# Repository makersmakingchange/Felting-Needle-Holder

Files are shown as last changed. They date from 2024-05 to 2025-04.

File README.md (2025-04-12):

<!---  Open Source Assistive Technology: GitHub Readme Template Version 1.1 (2024-Mar-15)  --->

<!---  TITLE  --->
# Felting Needle Holder

<!---  SUMMARY  --->
The Felting Needle Holder is an open assistive technology device intended to make it easier to hold and manipulate a felting needle. The holder is ball-shaped with a diameter of 50 mm, and is comprised of four 3D printed parts. This aid is designed to be used with a felting needle that has a metal shaft with a bent end (e.g., [DIMENSIONS Replacement Felting Needles 72-73664](https://www.amazon.ca/Dimensions-Needlecrafts-Feltworks-Replacement-Felting/dp/B004W8TGIS)).

The holder consists of several 3D printed parts. No additional hardware is required. The overall cost of materials is about $1.

The Felting Needle Holder is an open assistive technology (OpenAT). Under the terms of the open source licenses, the device may be built, used, and improved upon by anyone.

Last Updated: 2024-May-16
The latest version (1.0) now includes a cover for the needle and labels to help indicate the direction to spin the ball to open or close it. The previous version (0.2) was built and tested by at least one user.

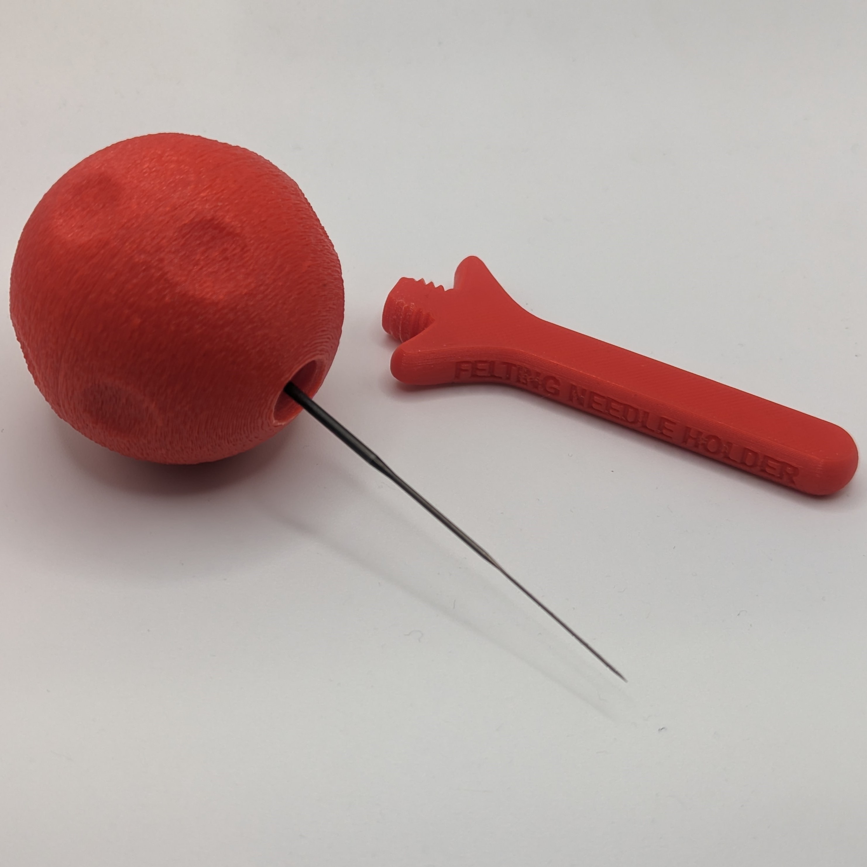
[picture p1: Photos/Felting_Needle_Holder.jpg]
A ball-shaped Felting Needle Holder.


## More info at
- [Makers Making Change Assistive Device Library Listing](https://www.makersmakingchange.com/s/product/felting-needle-holder/01tJR000004E3gVYAS)

## How to Obtain the Device
### 1. Do-it-Yourself (DIY) or Do-it-Together (DIT)

This is an open-source assistive technology, so anyone is free to build it. All of the files and instructions required to build the device are contained within this repository. Refer to the Maker Guide below.

### 2. Request a build of this device

You may also submit a build request through the [Makers Making Change Assistive Device Library Listing](https://www.makersmakingchange.com/s/product/felting-needle-holder/01tJR000004E3gVYAS) to have a volunteer maker build the device. As the requestor, you are responsible for reimbursing the maker for the cost of materials and any shipping.

### 3. Build this device for someone else

If you have the skills and equipment to build this device, and would like to donate your time to create the device for someone who needs it, visit the [MMC Maker Wanted](https://makersmakingchange.com/maker-wanted/) section.

## Build Instructions

### 1. Read through the Maker Guide

The [Maker Guide](/Documentation/Felting_Needle_Holder_Maker_Guide.pdf)  contains all the necessary information to build this device, including tool lists, assembly instructions, and testing.

### 2. Order the Off-The-Shelf Components

The [Bill of Materials](/Documentation/Felting_Needle_Holder_BOM.xlsx) lists all of the parts and components required to build the device.

### 3. Print the 3D Printable components

All of the files and individual print files can be in the [/Build_Files/3D_Printing_Files](/Build_Files/3D_Printing_Files/) folder.

### 4. Assemble the Felting Needle Holder

Reference the Assembly Guide section of the [Maker Guide](/Documentation/Felting_Needle_Holder_Maker_Guide.pdf) for the tools and steps required to build each portion.

## How to improve this Device
As open source assistive technology, you are welcomed and encouraged to improve upon the design. 

## Files
### Documentation
| Document             | Version | Link |
|----------------------|---------|------|
| Design Rationale     | 1.0     | [Felting_Needle_Holder_Design_Rationale](/Documentation/Felting_Needle_Holder_Design_Rationale.pdf)     |
| Maker Guide          | 1.0     | [Felting_Needle_Holder_Maker_Checklist](/Documentation/Felting_Needle_Holder_Maker_Guide.pdf)     |
| Bill of Materials    | 1.0     | [Felting_Needle_Holder_Bill_of_Materials](/Documentation/Felting_Needle_Holder_BOM.xlsx)     |
| User Guide           | 1.0     | [Felting_Needle_Holder_User_Guide](/Documentation/Felting_Needle_Holder_User_Guide.pdf)    |
| Changelog            | 1.0     | [Changelog](CHANGES.txt)     |

### Design Files
<!--- DESIGN FILES --->
 - [CAD Files](/Design_Files/CAD_Design_Files)

<!--- BUILD FILES --->
### Build Files
 - [3D Printing Files](/Build_Files/3D_Printing_Files)

<!--- ATTRIBUTION --->
## Attribution

This device was designed by the Neil Squire Society / Makers Making Change.

<!--- This is the attribution for the template. --->
The documentation template was created by Makers Making Change / Neil Squire Society and is used under a CC BY-SA 4.0 license. It is available at the following link: [https://github.com/makersmakingchange/OpenAT-Template](https://github.com/makersmakingchange/OpenAT-Template)

<!--- CONTRIBUTORS --->
### Contributors

 - Zee Kesler. Initial idea and design challenge.
 - Jake McIvor, Neil Squire Society. Design and documentation.

<!--- LICENSE Add the year(s) for the copyright and the Designer Name. You may use the standard set of open licenses or choose your own for the hardware, software, and accompanying materials. --->
## License
Copyright (c) 2022-2024 Neil Squire Society.

This repository describes Open Hardware:
 - Everything needed or used to design, make, test, or prepare the Felting Needle Holder is licensed under the [CERN 2.0 Weakly Reciprocal license (CERN-OHL-W v2) or later](https://cern.ch/cern-ohl ) .
 - Accompanying material such as instruction manuals, videos, and other copyrightable works that are useful but not necessary to design, make, test, or prepare the Felting Needle Holder are published under a [Creative Commons Attribution-ShareAlike 4.0 license (CC BY-SA 4.0)](https://creativecommons.org/licenses/by-sa/4.0/) .

You may redistribute and modify this documentation and make products using it under the terms of the [CERN-OHL-W v2](https://cern.ch/cern-ohl).
This documentation is distributed WITHOUT ANY EXPRESS OR IMPLIED WARRANTY, INCLUDING OF MERCHANTABILITY, SATISFACTORY QUALITY AND FITNESS FOR A PARTICULAR PURPOSE.
Please see the CERN-OHL-W v2 for applicable conditions.

Source Location: https://github.com/makersmakingchange/Felting-Needle-Holder

---

<!-- ABOUT MMC START -->
## About Makers Making Change
[Makers Making Change Logo](https://www.makersmakingchange.com/)

Makers Making Change is a program of [Neil Squire](https://www.neilsquire.ca/), a Canadian non-profit that uses technology, knowledge, and passion to empower people with disabilities.

Makers Making Change leverages the capacity of community based Makers, Disability Professionals and Volunteers to develop and deliver affordable Open Source Assistive Technologies.

 - Website: [www.MakersMakingChange.com](https://www.makersmakingchange.com/)
 - GitHub: [makersmakingchange](https://github.com/makersmakingchange)
 - Bluesky: [@makersmakingchange.bsky.social](https://bsky.app/profile/makersmakingchange.bsky.social)
 - Instagram: [@makersmakingchange](https://www.instagram.com/makersmakingchange)
 - Facebook: [makersmakechange](https://www.facebook.com/makersmakechange)
 - LinkedIn: [Neil Squire Society](https://www.linkedin.com/company/neil-squire-society/)
 - Thingiverse: [makersmakingchange](https://www.thingiverse.com/makersmakingchange/about)
 - Printables: [MakersMakingChange](https://www.printables.com/@MakersMakingChange)

### Contact Us
For technical questions, to get involved, or to share your experience we encourage you to [visit our website](https://www.makersmakingchange.com/) or [contact us](https://www.makersmakingchange.com/s/contact).
<!-- ABOUT MMC END -->

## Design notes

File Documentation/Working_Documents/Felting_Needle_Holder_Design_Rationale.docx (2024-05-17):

# Introduction

Needle felting requires a user to repeatedly insert and remove a metal felting needle into and out of the material. A holder is often used to hold one or more of the needles. Typical holders are quite narrow.

# Research

No commercially available ball shaped felting needle holders were found. A large variety of cylindrical wooden holders are available, and these are relatively cost effective (e.g., 10 for ~$20 (https://www.amazon.ca/EXCEART-Needle-Handles-Felting-Needlework/dp/B09HV1QX2X))

# Requirements

## Goals

G01 | A ball-shaped holder that is easier to grip.
G02 | No tools are required to insert, swap, and remove needle.
G03 | Minimal or no hardware.

## Functional Requirements

F01 | Device must securely hold one standard metal felting needle.
F02 | Device must allow for the needle to be swapped out for a replacement.

## Non-functional Requirement

NF01 | Design should allow for multiple sizes of holder.

## Constraints

C01 | Design released under open-source license.
C02 | Components must be manufacturable on consumer-grade FFF 3D printers.
C03 | Components must be manufacturable using commonly available FFF filaments such as PLA.

# Detailed Design

## Felting Needle

The dimensions of a DIMENSIONS felting needle (https://www.amazon.com/Dimensions-Needlecrafts-Feltworks-Replacement-Felting/dp/B004W8TGIS) were measured with a pair of digital calipers. The needle has a diameter of 1.8 mm. The top portion is bent at a 90° angle and extends about 3.5 mm from the main portion. The overall length of the needle is 78 mm.

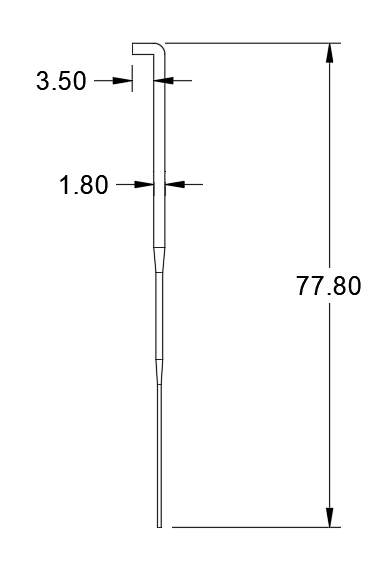
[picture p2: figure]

Figure 1: DIMENSION Felting Needle Dimensions.

## Architecture

The overall arrangement consists of four parts: Top, Bottom, Connector, and Cover. A Top and Bottom of a ball provide a larger gripping surface for the user. A Connector performs two functions: it connects the two parts of the ball together and is used to retain the needle. A Cover was later added so the ball could be stored with the needle inside with a reduce risk of either breaking the needle or the needle causing injury.

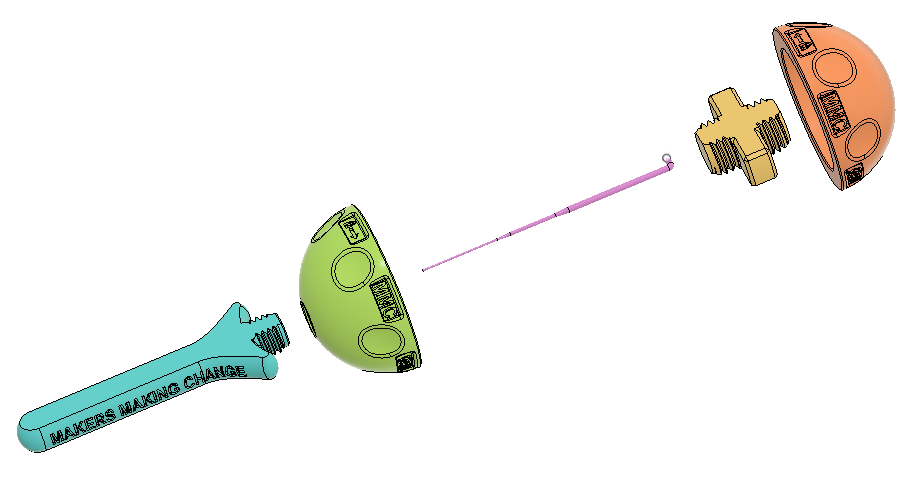
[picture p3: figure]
An exploded view of the Felting Needle Holder showing the Cover, Bottom, Needle, Connector, and Top.

Figure 2. Exploded View.

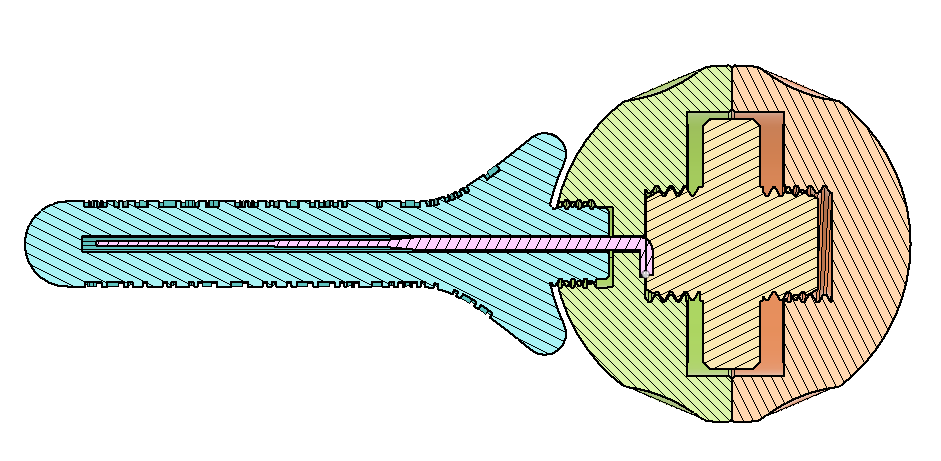
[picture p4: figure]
A cross section of the needle holder showing the needle captured by the connector

Figure 3. Felting Needle Holder Cross Section.

## Ball

The initial diameter of 50 mm for the ball was chosen based on recommendations for ergonomic handles. Additional user feedback would be helpful to determine a range of appropriate sizes for different users.

A pattern of divots was added around the ball to provide finger grips both during felting and opening and closing the ball.

Several labels were added to the ball. An arrow and a lock icon were added to provide visual indication of which direction the ball halves need to be rotated to lock it into place. An additional label was added to indicate the diameter of the ball (e.g., Ø50).

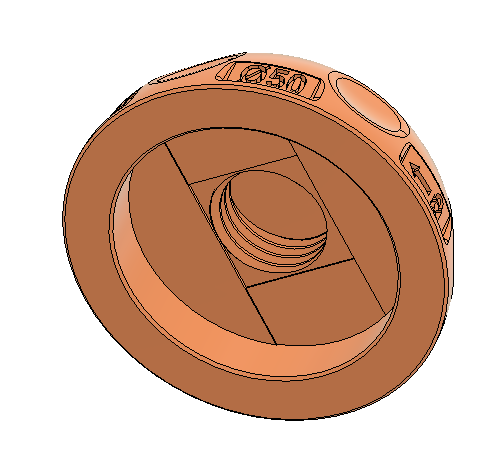
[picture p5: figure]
A CAD screenshot of the top.

Figure 4. Top Portion of Ball.

Both the top and the bottom use a right-handed M16X2 ISO Metric thread profile for the internal threads. The internal thread surfaces are offset by 0.1 mm to provide additional clearance for 3D printing.

To print without support, the inner surface of the ball has two sets of cuts to force bridging. The longest section of this bridge is 33 mm so some printers may struggle. Since these surfaces are internal, any reduced print quality is probably acceptable; those with printers that struggle to reliably bridge this distance can also enabled support.

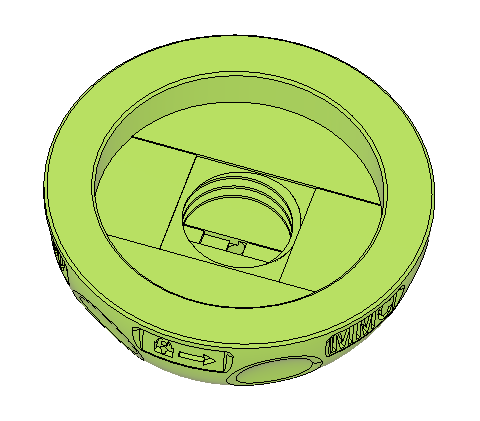
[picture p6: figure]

Figure 5. Bottom Portion of Ball.

The Bottom also has the internal thread for the connector and the corresponding bridging cuts. This side also has features for retaining and supporting the needle and connecting the cover.

The needle is retained using a cutout to fit the bent portion of the needle. This prevents the needle from rotating, and provides a surface that the Connector can compress the Needle into the Bottom. Bridging cuts were also added here to improve print quality.

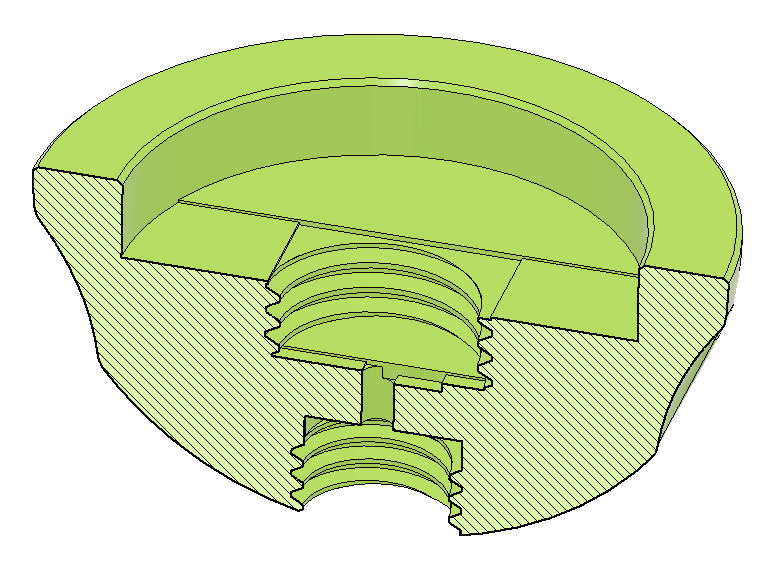
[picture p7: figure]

The bottom of the Bottom has a right-handed M12x1.75 ISO Metric internal thread to connect the Cover. These internal thread surfaces are also offset by 0.1 mm to provide additional clearance for 3D printing. The threads were made different sizes to match the smaller required size of the Cover as well as to ensure the parts can not be assembled incorrectly.

## Connector

The Connector retains the needle into the Bottom and connects the Top and Bottom. The Connector consists of two threaded portions for connecting to the top and bottom, and a middle section that can be used to tighten the connector without tools.

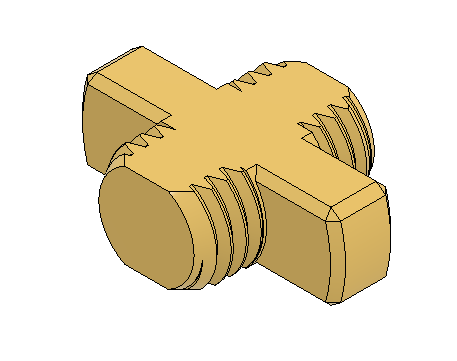
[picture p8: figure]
A CAD screenshot of the connector.

Figure 6. Connector.

The connector uses a right-handed M16X2 ISO Metric thread profile to match the threads on the ball parts. The cylindrical parts of the thread are truncated to allow the part to print on its side. Printing on the side improves print quality and strength.

## Cover

The Cover covers the needle when the holder is not in use. The Cover is an elongated truncated cylinder shape with an internal hole for the needle. One end of the Connector has external threads for connecting to the Bottom.

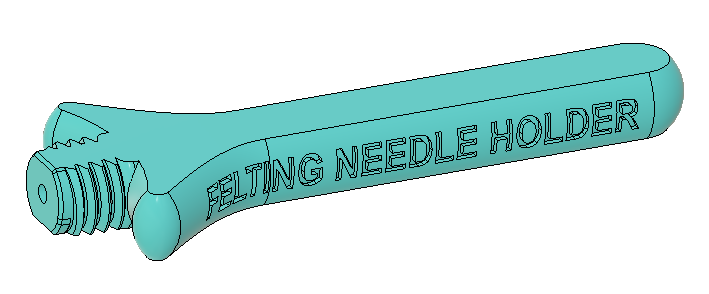
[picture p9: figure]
A CAD screenshot of the Connector.

The threads on the Cover are a right-handed M12x1.75 ISO Metric external thread to connect with the corresponding threads in the Bottom. Like the Connector, these threads are truncated so the part can print on its side for strength and print quality.

The hole for the needle has additional cuts to improve print quality for this horizontally printed hole.

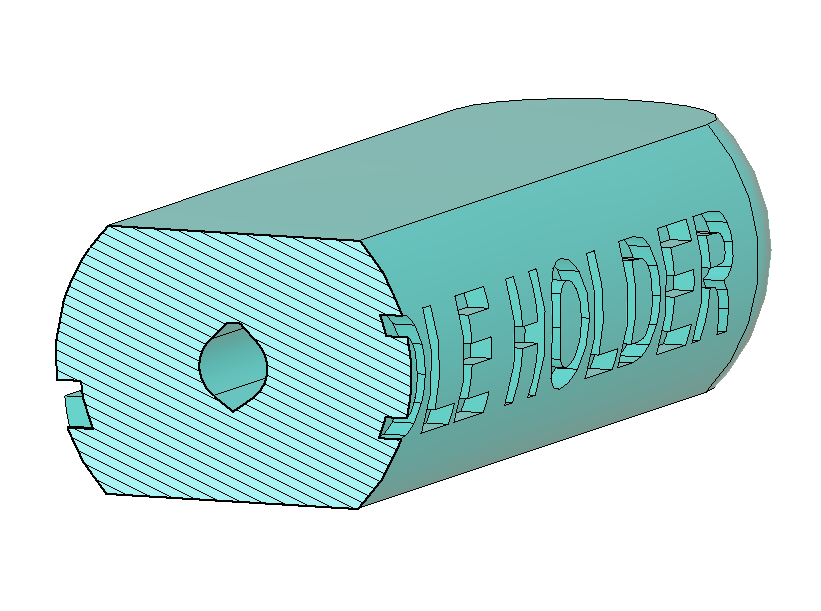
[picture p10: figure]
A CAD screenshot showing a cross section of the Connector through the needle hole. The top and bottom of the needle hole are modified to improve print quality.

Figure 7. Connector Cross-Section Showing Modified Needle Hole.

# V1.0

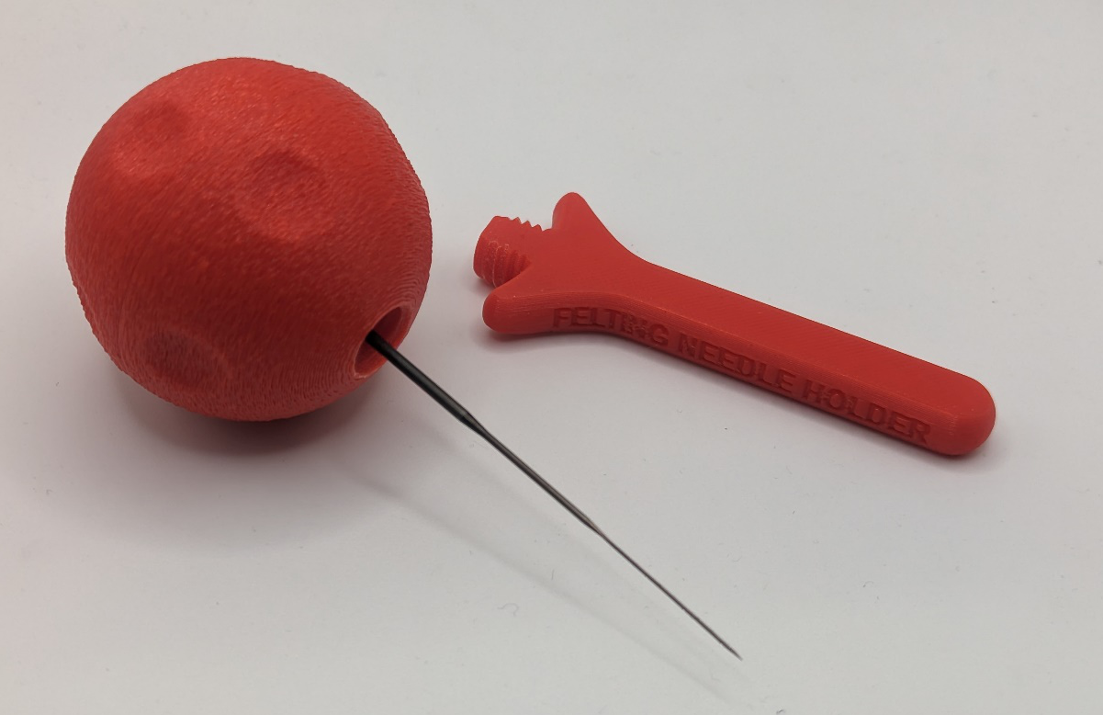
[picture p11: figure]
Photo of Felting Needle Holder assembled with Needle inserted.

## Opportunities for Improvement

1. Determine a range of appropriate sizes and create corresponding versions (e.g., small, medium, large).
2. Create a version that can hold multiple needles.
3. Experiment with different textures.

© 2022-2024 by Neil Squire Society. This work is licensed under the CC BY SA 4.0 License: http://creativecommons.org/licenses/by-sa/4.0 Files available at https://github.com/makersmakingchange/Felting-Needle-Holder Page 1 of 1

V1.0 | MARCH 2024 Felting Needle Holder Design Rationale

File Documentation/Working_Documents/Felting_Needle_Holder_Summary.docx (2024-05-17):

This document is intended to be a summary of a device to make it easier to add to the website.

# Product Information

## Product Name

Felting Needle Holder

## Device Category

Mark any relevant categories with an “X”:

| Adapted Toys
| Aids for Daily Living (ADL)
| Assistive Switches
| Communication Aids (AAC)
| Computer Access
| Environmental Controls
| Gaming
| Keyguard
| Kits
| LipSyncs
| Mounting
X | Recreation and Leisure
| Seating and Positioning
| Switch Interfaces
| Writing Aids

## User Value Statement

This ball-shaped aid can make it easier to hold and manipulate a felting needle.

## Designer

Makers Making Change

# Device Info

## Overview

The Felting Needle Holder is an aid for making it easier to hold and manipulate a felting needle. The holder is ball shaped with a diameter of 50 mm (~2 inch), between the size of a golf ball and a billiards ball.

## Disability Type

Select one or more disability types and mark with an “X”:

X | Agility / Dexterity
X | Arthritis
| Cognitive
| Hearing
| Mobility
| Mobility
X | Pain
| SCI
| Vision
| Other

## Disability Type Description

The Felting Needle Holder may be useful for people with limited hand strength and/or dexterity. This may include people with arthritis, Parkinson’s disease, muscular dystrophy, cerebral palsy, and stroke survivors. The device may also be helpful for children.

## How To Use

Once assembled, the Felting Needle Holder is intended to be held in the hand.

To assemble the Felting Needle Holder, the needle is inserted into the bottom of the ball. The threaded connector is used to fasten it in place and then the top is attached.

When the holder is not in use, the cover can be inserted over the needle to cover the sharp point.

## Estimated Cost

The estimated material cost of the device for a single build:

X | $0 - $10
| $11 - $25
| $26 - $50
| $51 - $100
| $101 - $250
| $250+

$1

## Attribution

Designed by Neil Squire Society / Makers Making Change

Contributors:

Zee Kessler. Original idea and design challenge.

Jake McIvor. Neil Squire Society. Design and documentation.

# Maker Info

## Project Skills

Mark the required project skills with an “X”:

X | 3D Printing
| Custom PCB
| Electronics
| Laser Cutting
| Mechanics
| Software
| Soldering
| Woodworking
| Other

## Skills Description

This is a simple build that consists of four 3D printed parts.

## Tools Needed

X | 3D Printer
| Common Hand Tools
| Common Power Tools
| Laser Cutter
| Soldering Iron
| Specialized Tooling

## Print time (hrs)

1.5 – 4 hours

## Assembly time (hrs)

15 min

## Build Instructions

This is a simple build that consists of four 3D printed parts.

- 1X 3D Printed Ball Top
- 1X 3D Printed Ball Bottom
- 1X 3D Printed Connector
- 1X 3D Printed Cover
- 1X Felting Needle (Not included)

## Download Link

https://github.com/makersmakingchange/Felting-Needle-Holder/archive/refs/heads/main.zip

## Project Link

# https://github.com/makersmakingchange/Felting-Needle-Holder

# License

## License

Hardware: CERN OHL-W

Software: n/a

Documentation: CC BY-SA

© 2022-2024 by Neil Squire Society. This work is licensed under the CC BY SA 4.0 License: http://creativecommons.org/licenses/by-sa/4.0 Files available at https://github.com/makersmakingchange/Felting-Needle-Holder Page 1 of 2

V1.0 | MAY 2024 Felting Needle Holder Summary

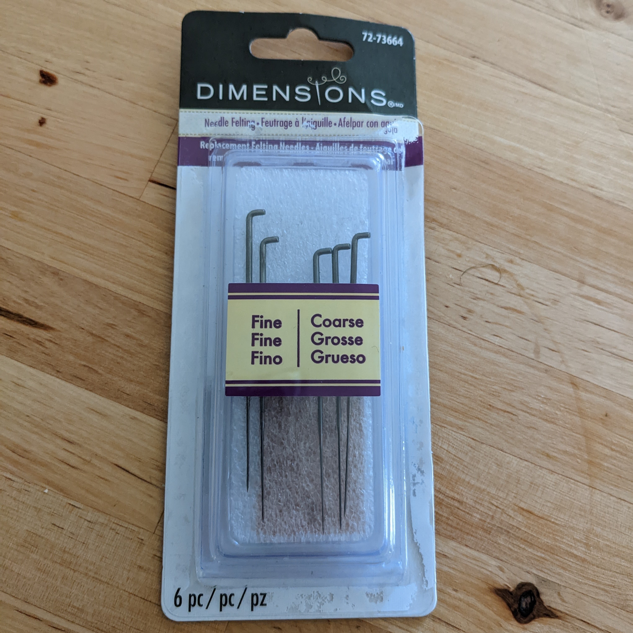
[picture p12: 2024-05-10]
Photos/Felting_Needles.jpg

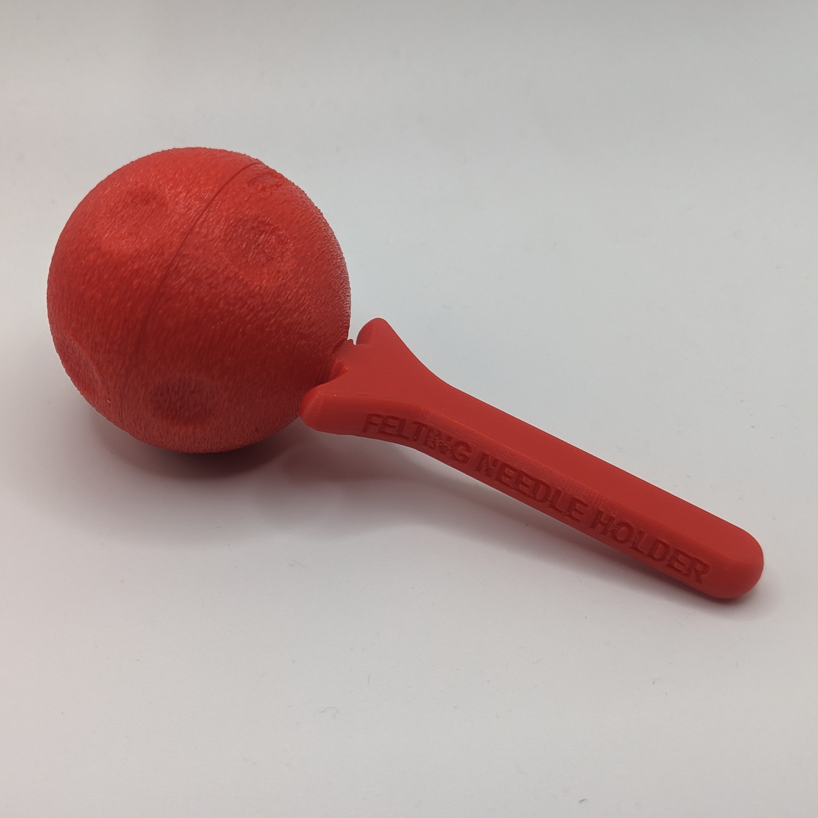
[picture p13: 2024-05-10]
Photos/Felting_Needle_Holder_Cover.jpg

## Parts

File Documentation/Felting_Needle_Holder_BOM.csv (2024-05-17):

Felting Needle Holder |  | Total Cost | Total Print time (hr) | Total filament (g)
Version: V1.0 | Last Updated: 2024-May-16 | $0.95 | 0.00 | 38
Commercial Parts:
Part type (Electrical, Mechanical, Sanitization, etc) | Part Name | Quantity Needed | Pkg Quantity | Price per package | Price per Unit | Price for qty needed | Link
<None>
3D Printed Parts ESTIMATED PRICING USING 1KG ROLL COST: | $25.00
Part | Description | Quantity Needed | TOTAL Mass (g) | Estimated Price | Print Time (Min) | Link
FNH_B50_Bottom.stl | Bottom half of ball | 1 | 14 | $0.35
FNH_B50_Top.stl | Top half of ball | 1 | 13 | $0.33
FNH_Connectort.stl | Threaded connector | 1 | 4 | $0.10
FNH_Cover.stl | Needle cover | 1 | 7 | $0.18
 |  |  |  | $-
 |  |  | Total Print Cost: | $0.95
Tools for Assembly
<None>
Alternatives (if there are other sources for some parts link them below)
Part and description | Link
Felting Needles | https://www.amazon.ca/Dimensions-Needlecrafts-Feltworks-Replacement-Felting/dp/B004W8TGIS

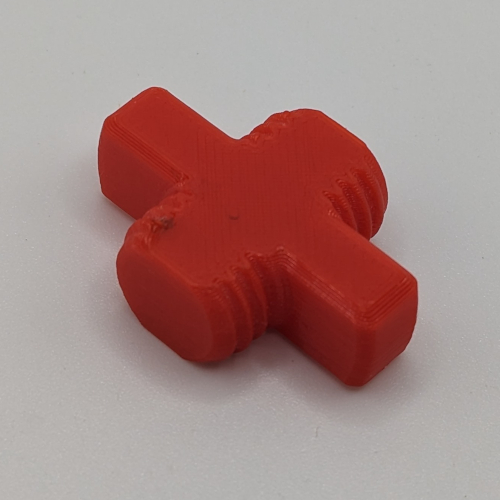
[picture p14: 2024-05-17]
Documentation/Working_Documents/Assets/Components/FNH_Connector.jpg

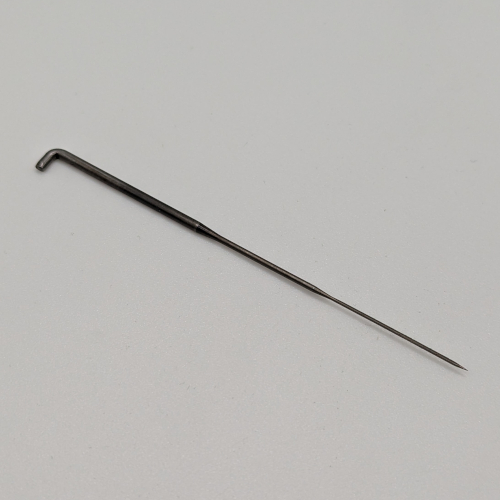
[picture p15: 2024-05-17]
Documentation/Working_Documents/Assets/Components/FNH_Needle.jpg

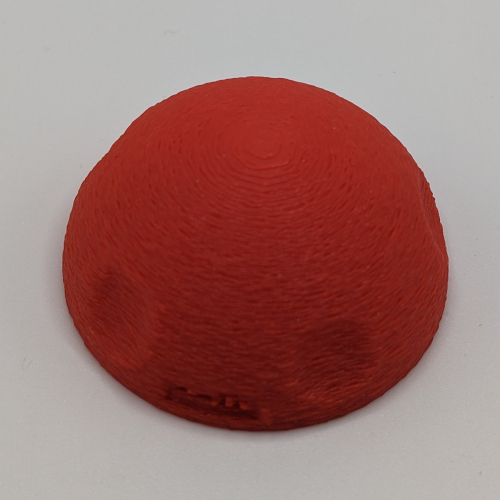
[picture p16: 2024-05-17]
Documentation/Working_Documents/Assets/Components/FNHB50_Top.jpg

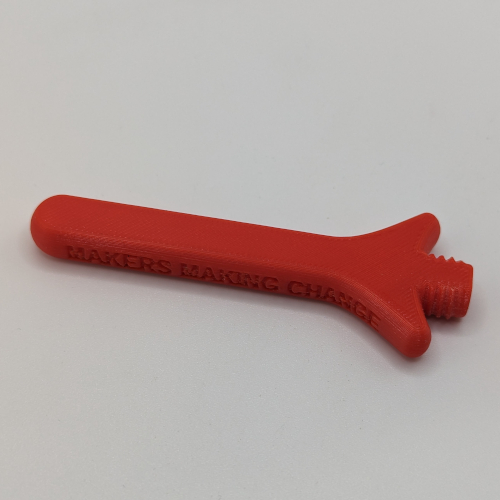
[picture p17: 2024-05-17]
Documentation/Working_Documents/Assets/Components/FNH_Cover.jpg

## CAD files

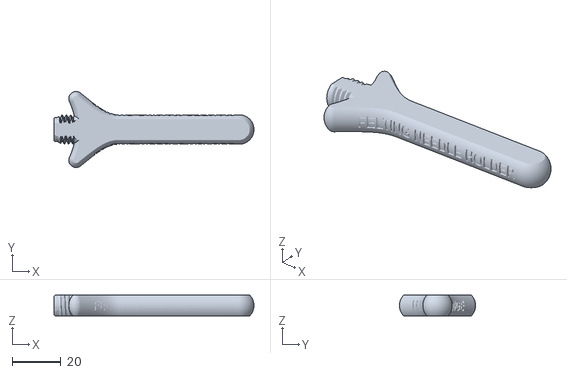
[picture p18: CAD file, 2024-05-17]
Build_Files/3D_Printing_Files/FNH_Cover.stl
81.8 x 31.1 x 8.49

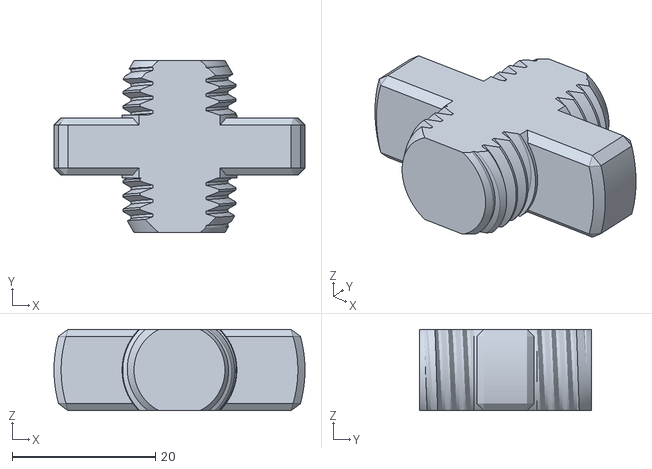
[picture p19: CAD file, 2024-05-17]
Build_Files/3D_Printing_Files/FNH_Connector.stl
35.0 x 24.0 x 11.3

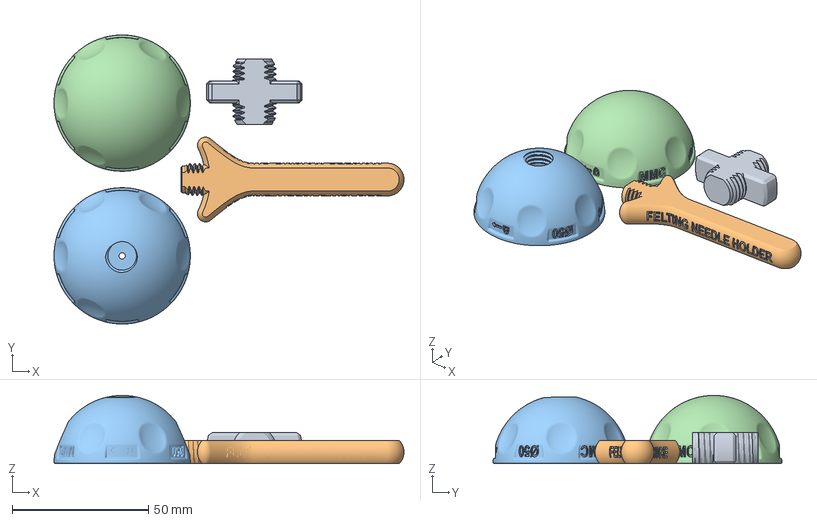
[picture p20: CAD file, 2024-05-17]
Build_Files/3D_Printing_Files/FNH_Set.3mf
128.3 x 106.0 x 25.0 mm
FNH_Connector.stl
FNH_Cover.stl
FNHB50_Bottom.stl
FNHB50_Top.stl

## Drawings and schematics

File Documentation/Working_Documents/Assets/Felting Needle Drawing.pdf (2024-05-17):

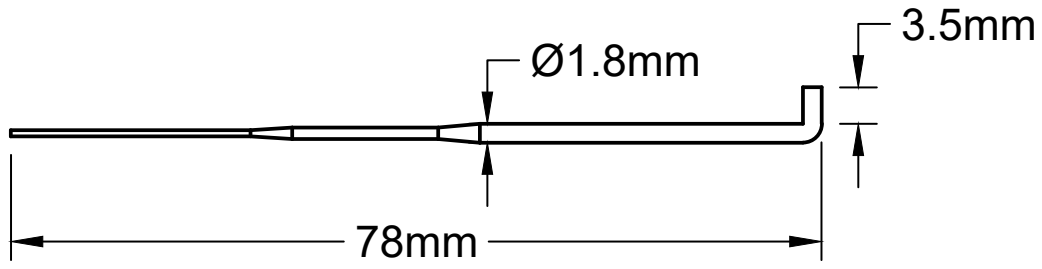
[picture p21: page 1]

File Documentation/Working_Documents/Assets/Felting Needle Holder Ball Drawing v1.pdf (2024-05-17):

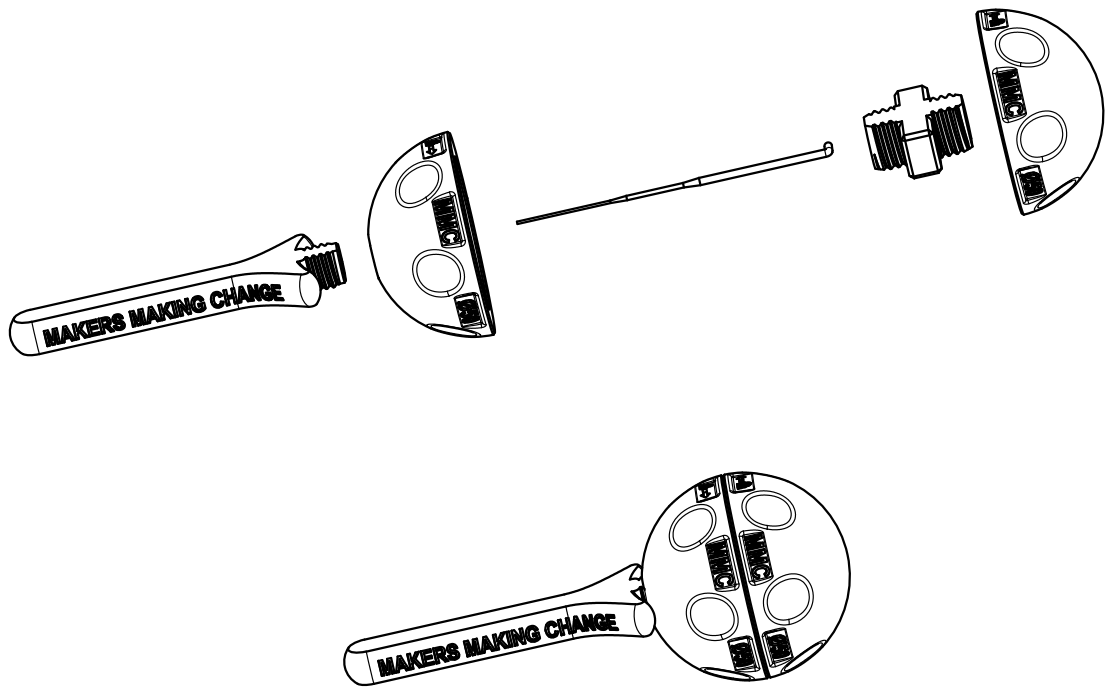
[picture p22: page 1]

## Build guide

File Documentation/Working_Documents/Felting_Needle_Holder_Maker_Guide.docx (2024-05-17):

# Overview

This document contains the necessary information to build a Felting Needle Holder.

# Maker Checklist

This list provides an overview of the steps required to build and deliver the device.

## Maker To Do List

- Read through the Maker Guide to become familiar with required components, tools, supplies, and safety gear and overall assembly steps.
- Talk to User about customization options (e.g., color, any special requests, etc.)
- Gather tools, supplies, and safety equipment.
- Assemble the device
- Test device
- Print “User Quick Guide”

## Items to Give to User

- Assembled, tested device
- “User Quick Guide”

# Tool List

No tools are required.

# Customization Guide

Different portions of the Felting Needle Holder can be printed in the user’s desired colors.

The Top and Bottom can be printed with a fuzzy setting on the outside to make them more grippy.

# 3D Printing Guide

## 3D Printing Summary

Metrics | V1.0
Total Print Time (hr:min) | 4:00
Total Number of Components | 4
Typical Total Mass (g) | 35
Typical Number of Print Setups | 1

## 3D Printing Settings

Print File Name | Qty | Total Print Time (hr:min) | Mass (g) | Infill (%) | Support (Y/N) | Layer Height/ Nozzle Diameter (mm) | Notes
FNHB50_Top.stl | 1 | 0:30 | 13 | 15 | N | 0.2/0.4
FNHB50_Bottom.stl | 1 | 0:30 | 14 | 15 | N | 0.2/0.4
FNH_Connector.stl | 1 | 0:11 | 4 | 15 | N | 0.2/0.4
FNH_Cover.stl | 1 | 0:20 | 7 | 15 | N | 0.2/0.4

The Top and Bottom can be printed with a fuzzy setting on the outside to make them more grippy – check the settings for your slicer.

## Post-processing

- Check for any bits of loose filament or sharp edges.
- Check to make sure the Cover threads into the Bottom cleanly.
- Check that the Connector threads into the Bottom.
- Check that the Connector threads into the Top.

# Assembly Guide

### Part A: Components

A1 | FNHB50 Bottom | QTY 1 | A2 | Felting Needle | QTY 1 | A3 | FNH Connector | QTY 1

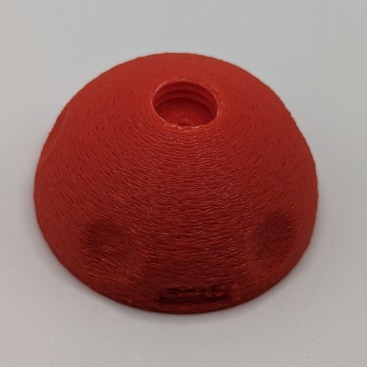
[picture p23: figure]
Felting Needle Holder Bottom
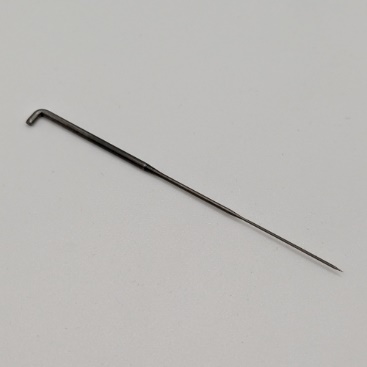
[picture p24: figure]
Felting Needle
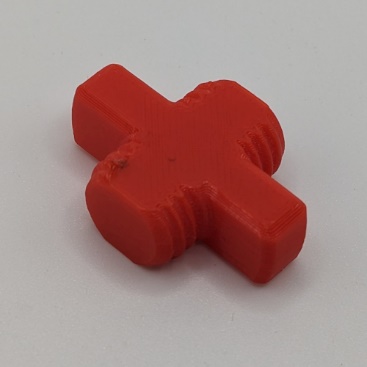
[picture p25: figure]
Felting Needle Holder Connector

od.
A4 | FNH Top | QTY 1 | A5 | FNH Connector | QTY 1

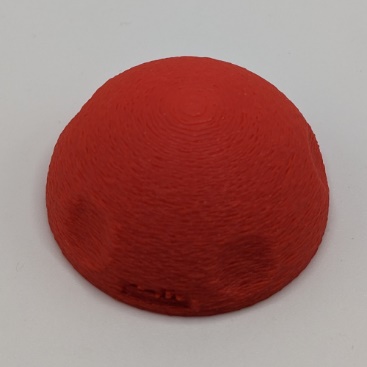
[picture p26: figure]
Felting Needle Holder Top
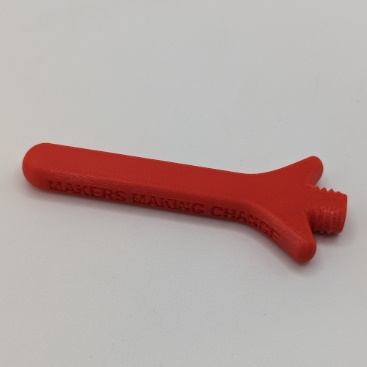
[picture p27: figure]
Felting Needle Holder Cover

### Part A: Tools

- None

### Part A: Personal Protective Equipment (PPE)

- None

### Part A: Assembly Instructions

#### Step 1: Insert Needle into Bottom

Insert the felting needle into the Bottom. Align the bent tip with the depression in the Bottom.

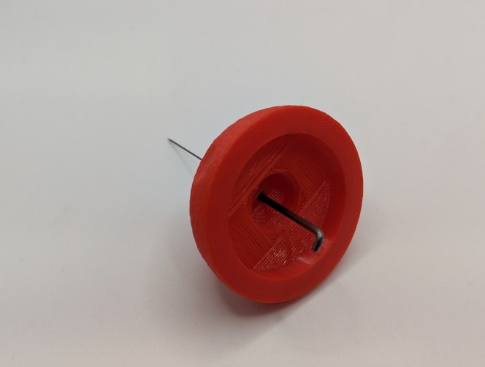
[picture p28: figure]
The Felting Needle being inserted into the Bottom.

#### Step 2: Thread Connector into Bottom

Thread the Connector into the Bottom. Rotate it clockwise until snug.

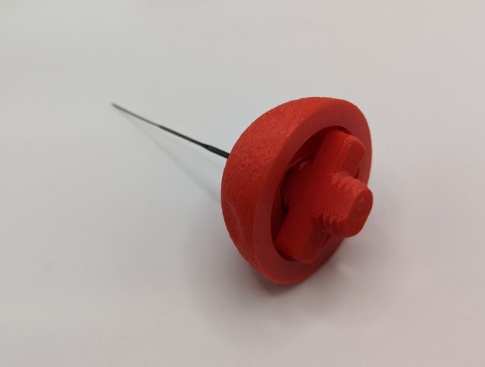
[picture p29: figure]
The Connector threading into the Bottom.

#### Step 3: Attach Top to Connector

Attach the Top to the Connector. Hold the Bottom stationary and rotate the Top clockwise with the needle facing away. You can also refer to the lock labels.

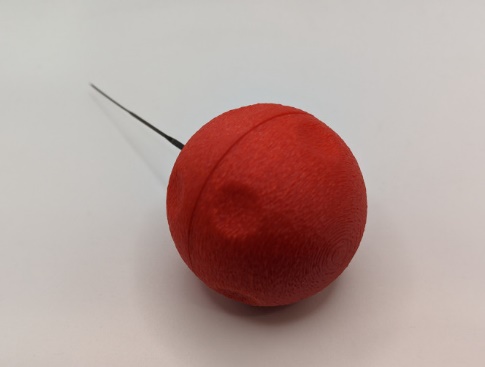
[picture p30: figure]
Threading the Top on to the Connector to match up with the Bottom.

#### Step 3: Attach Cover to Bottom

Insert the needle into the Cover. Tighten the threads into the Bottom.

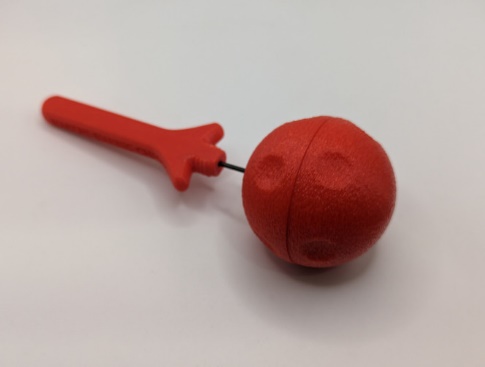
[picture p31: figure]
Inserting the Needle into the Cover and then threading the Cover into the Bottom.

© 2022-2024 by Neil Squire Society. This work is licensed under the CC BY SA 4.0 License: http://creativecommons.org/licenses/by-sa/4.0 Files available at https://makersmakingchange.com/project/felting-needle-holder/ Page 1 of 1

V1.0 | MARCH 2024 Felting Needle Holder maker Guide

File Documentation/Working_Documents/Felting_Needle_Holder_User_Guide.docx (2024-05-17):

## Introduction

The Felting Needle Holder is an aid to make it easier to hold and manipulate a felting needle. The aid is ball shaped and consists of three 3D printed parts that screw together: a top, a bottom, and a connector.

## Features

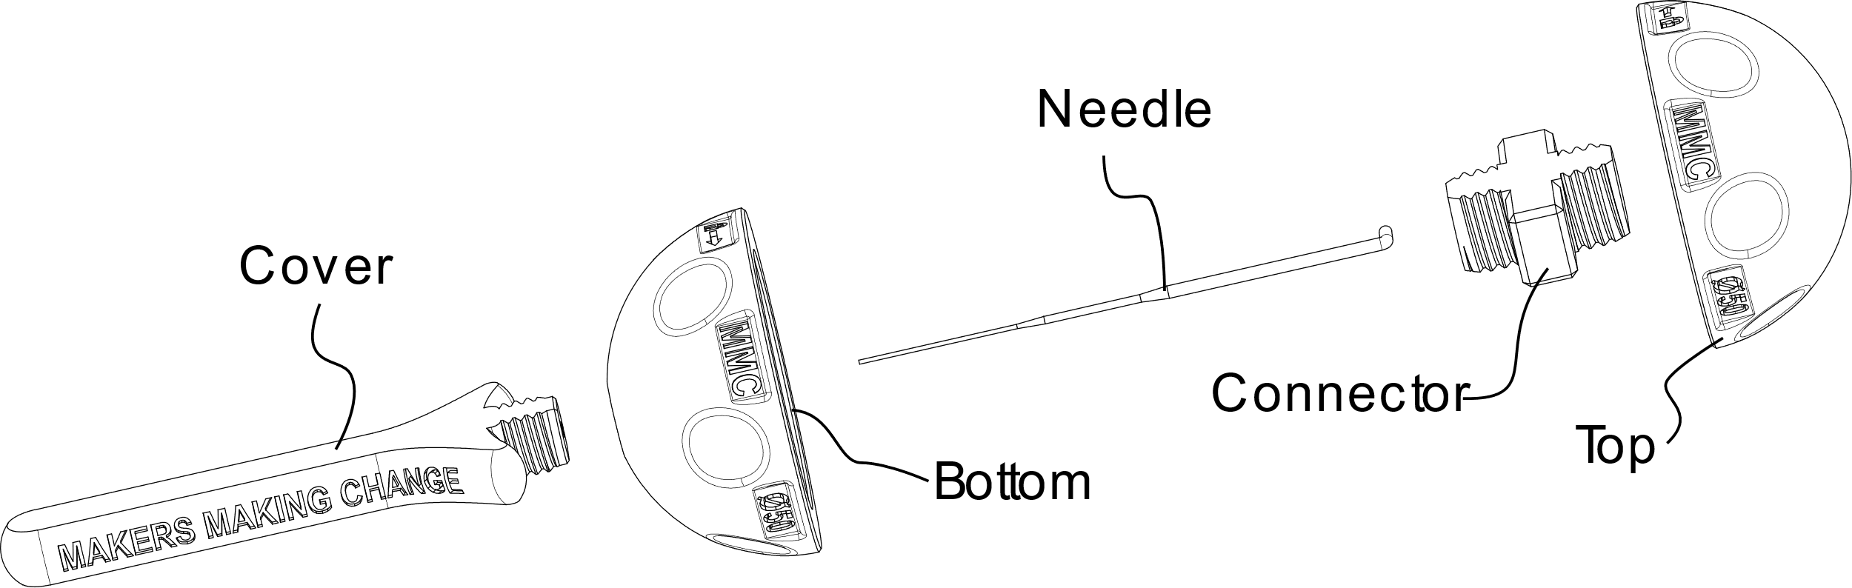
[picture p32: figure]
Assembly diagram for the Felting Needle Holder. The needle goes into the bottom, then the connector threads into the bottom, then the top connects to the connector. The cover can be added over the needle.

## Usage

To insert, replace, or remove the needle, the two halves of the ball need to be opened by twisting them. Once the needle is installed, the ball can be gripped within the hand for felting.

### Opening Ball

1. To open the ball, locate the half with the hole. Looking down on the top, hold the bottom half and turn the top half counter-clockwise.
2. Remove the connector by turning it counter-clockwise.

### Inserting Needle

1. Insert the felting needle into the bottom half. Insert the needle into the hole from the inside of the bottom half.
2. Rotate the needle so that the bent portion rests within the groove in the bottom half of the ball.
3. Thread the connector into the hole to secure the needle into place. The connector should be rotated clockwise until finger tight.

### Closing Ball

1. Thread the top half onto the connector. Looking down on the rounded part of the top half, rotate the top half counterclockwise to secure it to the bottom half.

## Compatibility

Designed for Felting Needles with a 1.8 mm diameter and a 3.5 mm L-shaped bend at the end (e.g., DIMENSIONS 72-73664 (https://www.amazon.ca/Dimensions-Needlecrafts-Feltworks-Replacement-Felting/dp/B004W8TGIS))

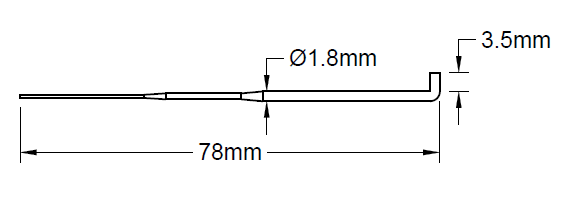
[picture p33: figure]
A scaled diagram of a compatible felting needle.

## Specifications

Ball Size | 50 mm Diameter

## Cleaning

The Holder can be wiped with a damp cloth. The Holder can also be cleaned by scrubbing with warm water and dish soap. Do not expose to high heat like a dishwasher. Do not use harsh cleaners.

© 2022-2024 by Neil Squire Society. This work is licensed under the CC BY SA 4.0 License: http://creativecommons.org/licenses/by-sa/4.0 Files available at https://makersmakingchange.com/project/felting-needle-holder/ Page 1 of 1

V1.0 | MAY 2024 Felting Needle Holder user Guide

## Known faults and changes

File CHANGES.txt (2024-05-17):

Version 1.0 | 2024-May-16
 - Added threaded cover
 - Full documentation release

Version 0.3 | 2023-Mar-15
 - Initial user guide

Version 0.2 | 2022-Oct-21
 - Added lock labels and arrows

Version 0.1 | 2022-Oct-19
 - Initial prototype: two spherical halves with threaded connector
